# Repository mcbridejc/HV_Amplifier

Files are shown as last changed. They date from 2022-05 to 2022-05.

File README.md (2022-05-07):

High Voltage Amplifier
======================

A high-voltage amplifier takes a lower voltage input signal -- e.g. from a 
function generator of some sort -- and amplifies it to a high voltage. In this
case, the output range is -200V to +200V. High voltage amplifiers can be used
for a variety of applications, such as driving piezos, or digital microfluidics
electrodes. 

This board was created in KiCad 6.0.4. 

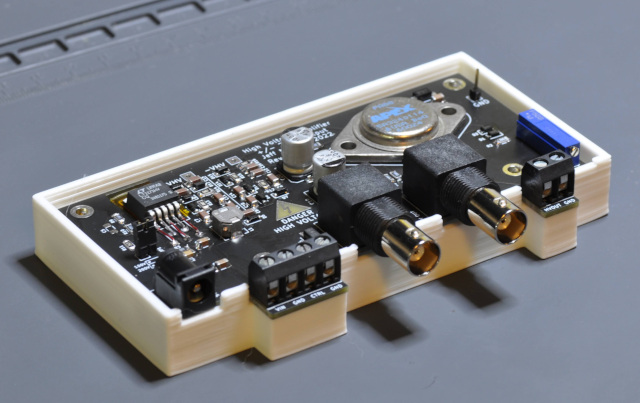
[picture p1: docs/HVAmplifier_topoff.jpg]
HV Amplifier


## A WARNING

This project can be dangerous. 200V is sufficient to kill you under
the right conditions. Even under the best conditions, it can give you a 
painful shock. You should not build this unless you know what you're doing.
If you do build this, you should handle it with caution. Be very careful about
what you touch when it is energized. Don't touch it with both hands
simultaneously. If you don't have to have it exposed, enclose it. Insulate
any wiring connected to the HV output.

## Description

This design uses the Apex PA88 high-voltage op-amp. These are fairly expensive
(~$250) at mouser, but I was able to find one for much cheaper on Ebay when I
built this. It also has a switching power supply which generates the positive
and negative high voltage rails from a 9V input. 

It can be operated at 100V, or 200V, based on whether the jumper JP1 is shorted.

The gain (Output voltage / control voltage) is adjustable from 15.9x to 60.2x,
using the potentiometer. At maximum gain, an input of 3.3V will provide an
output of 199V. 

When idle, it draws about 40mA when operating at 100V, and about 80mA at 200V. It
should be able to source about 4mA, although I have not tested under this kind
of load. For my application the current draw is much less. At some point I may
stress test it, but I am putting it off in case this test proves to be destructive!

## Enclosure 

I have provided some mesh files for a 3D printable enclosure. It requires some
M3 heat inserts (like [these](https://www.amazon.com/initeq-M3-0-5-Threaded-Inserts-Printing/dp/B073W2898C/))
and 18-23mm long M3 screws (like [these](https://www.amazon.com/M3-0-5-Stainless-Socket-Screws-Coverage/dp/B09B3992F4/)) 
to assemble. The STLs can be found in the [enclosure](enclosure/) directory.

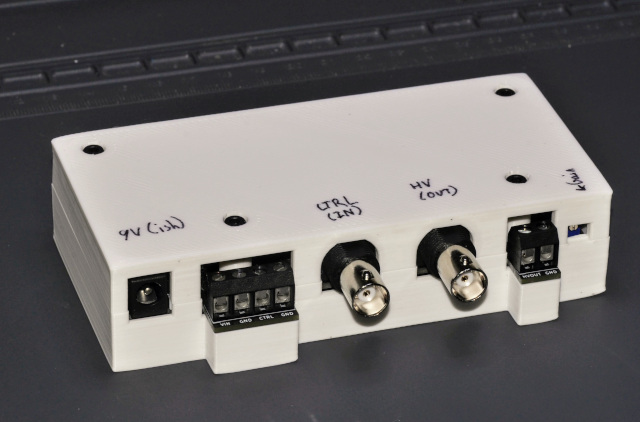
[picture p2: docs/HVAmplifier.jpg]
HV Amplifier


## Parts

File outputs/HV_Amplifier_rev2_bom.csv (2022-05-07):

Component | References | Value | Mfg Part Number | Package | Part Description | Voltage | Quantity Per PCB
1 | C3-C4 | 0.1u |  | 1206 | CAP CER 0.1UF 450V X7T 1206 | 450V | 2
2 | C6-C16 | 0.22u |  | 1206 | CAP CER 0.22UF 100V X7R 1206 | 100V | 11
3 | C19-C20 | 1.8u | UUB2G1R8MNL1GS |  |  | 400V | 2
4 | C17-C18 | 10u |  | 1206 | CAP CER 10UF 25V X5R 1206 | 25V | 2
5 | C1 | 15pF |  | 1206 | CAP CER 15PF 50V C0G/NP0 1206 | 50V | 1
6 | C2 | 1u |  | 1206 | CAP CER 1UF 16V X7R 1206 | 16V | 1
7 | D1-D2 D5-D15 | DSS120U | DSS120U | SOD-123F | SCHOTTKY 200V SOD-123FL |  | 13
8 | D16 | SMA6J5.0CA | SMA6J5.0CA | SMA | TVS DIODE 5VWM 9.2VC DO214AC TR |  | 1
9 | D3-D4 | SMAJ200A | SMAJ200A-TP | SMA | TVS DIODE 200V 324V DO214AC |  | 2
10 | J2 J4 | BNC | RF1-01K-D-00-50-BK-HDW |  | BNC RA PCB 50 4GHZ ZINC BODY NI |  | 2
11 | J3 | Barrel_Jack_Switch | PJ-202AH |  | CONN PWR JACK 2X5.5MM KINKED PIN |  | 1
12 | J1 | CTRL_TERM | 31101104 |  | TERM BLK 4P SIDE ENT 5.08MM PCB |  | 1
13 | J5 | Screw_Terminal_01x02 | 31101102 |  | TERM BLK 2P SIDE ENT 5.08MM PCB |  | 1
14 | JP1 | 100/200V SEL |  |  |  |  | 1
15 | L1 | 68uH | SPM6545VT-680M-D |  | FIXED IND 68UH 1.7A 340 MOHM SMD |  | 1
16 | R12-R16 | 10 |  | 1206 | RES 10 OHM 1% 1/4W 1206 |  | 5
17 | R1 R7 | 100 |  | 1206 | RES SMD 100 OHM 1% 1/4W 1206 |  | 2
18 | R8 R11 | 12.4k |  | 1206 | RES 12.4K OHM 1% 1/4W 1206 |  | 2
19 | R6 | 150 |  | 1206 | RES 150 OHM 1% 1/2W 1206 |  | 1
20 | R2 | 16.9k |  | 1206 | RES SMD 16.9K OHM 1% 1/4W 1206 |  | 1
21 | R3 | 1k |  | 1206 | RES 1K OHM 1% 1/2W 1206 |  | 1
22 | R4-R5 R9-R10 | 499k |  | 1206 | RES 499K OHM 1% 1/4W 1206 |  | 4
23 | RV1 | 50k | CT20EP503 |  | TRIMMER 50K OHM 0.5W PC PIN SIDE |  | 1
24 | U2 | LT117xHV | LT1171HVCQ |  | IC REG MULTI CONFG ADJ 5DDPAK |  | 1
25 | U1 | PA88 |  | TO-3-8 |  |  | 1
Component Groups: | 26
Component Count: | 62
Fitted Components: | 61
Number of PCBs: | 1
Total components: | 61
Schematic Version: | 2
Schematic Date: | 2022-05-06
PCB Variant: | [u'default']
BoM Date: | Fri 06 May 2022 05:38:52 PM PDT
Schematic Source: | HV_Amplifier.kicad_sch
KiCad Version: | Eeschema 6.0.4-6f826c9f35~116~ubuntu21.10.1

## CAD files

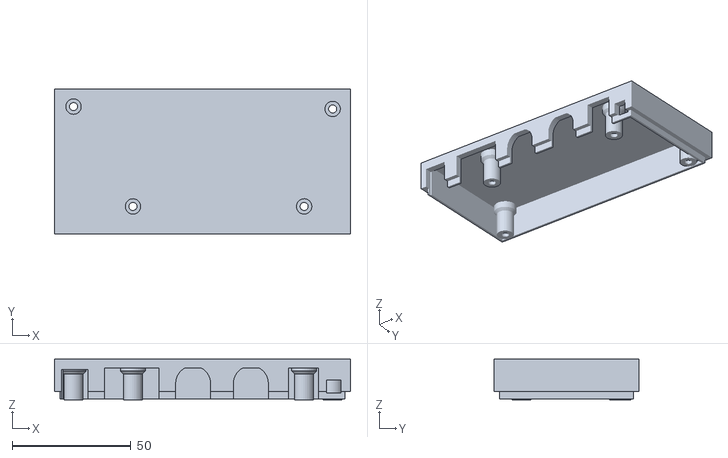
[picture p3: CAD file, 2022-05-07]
enclosure/HV_Amplifier_Enclosure_Top.stl
124.5 x 60.8 x 17.1

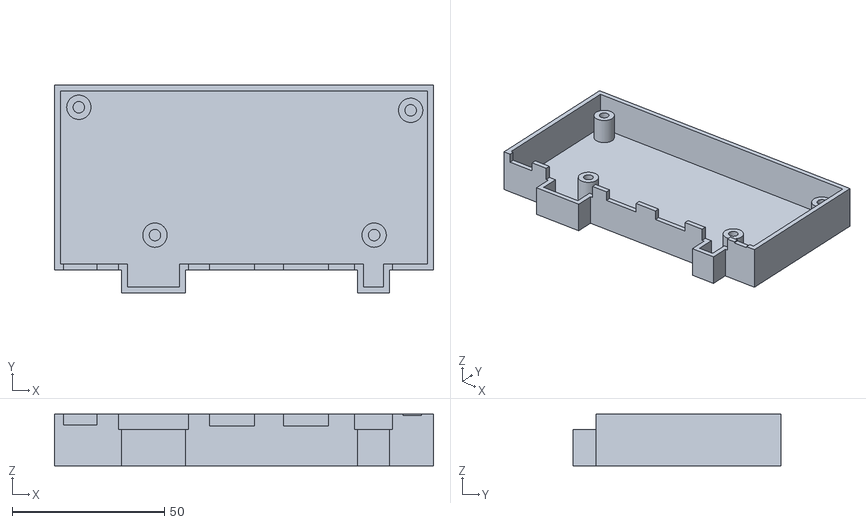
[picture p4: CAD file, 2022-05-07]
enclosure/HV_Amplifier_Enclosure_Bottom.stl
124.5 x 68.3 x 17.0

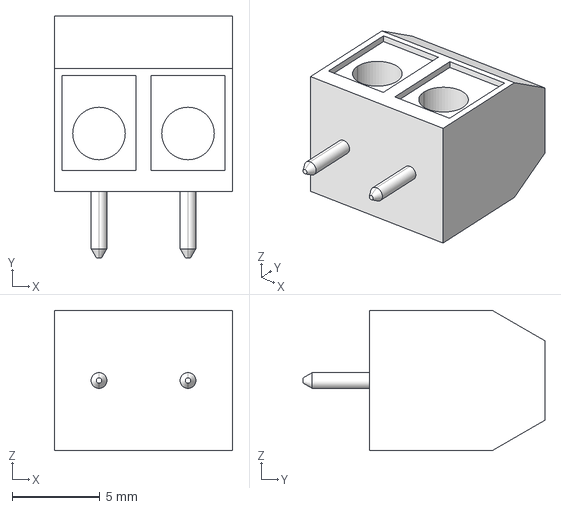
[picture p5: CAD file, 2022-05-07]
3dmodels/31101102.stp
10.2 x 13.8 x 8.00 mm

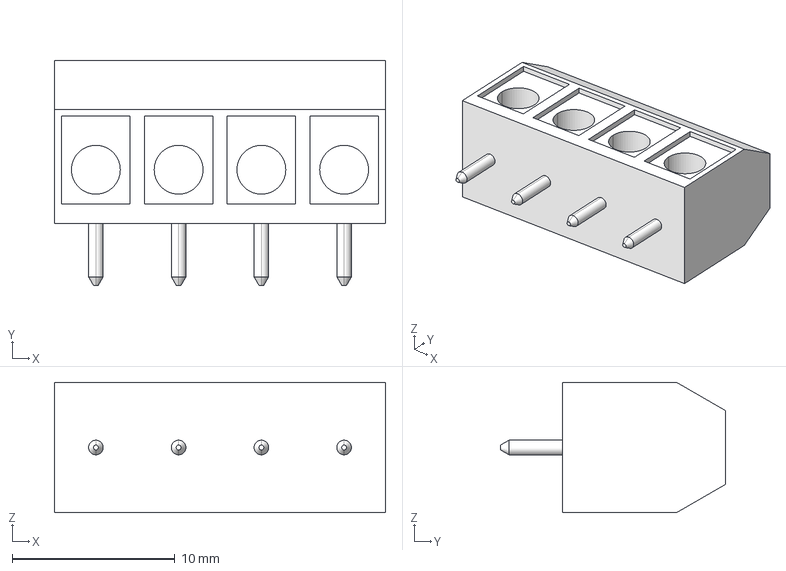
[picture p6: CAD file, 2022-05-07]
3dmodels/31101104.stp
20.3 x 13.8 x 8.00 mm

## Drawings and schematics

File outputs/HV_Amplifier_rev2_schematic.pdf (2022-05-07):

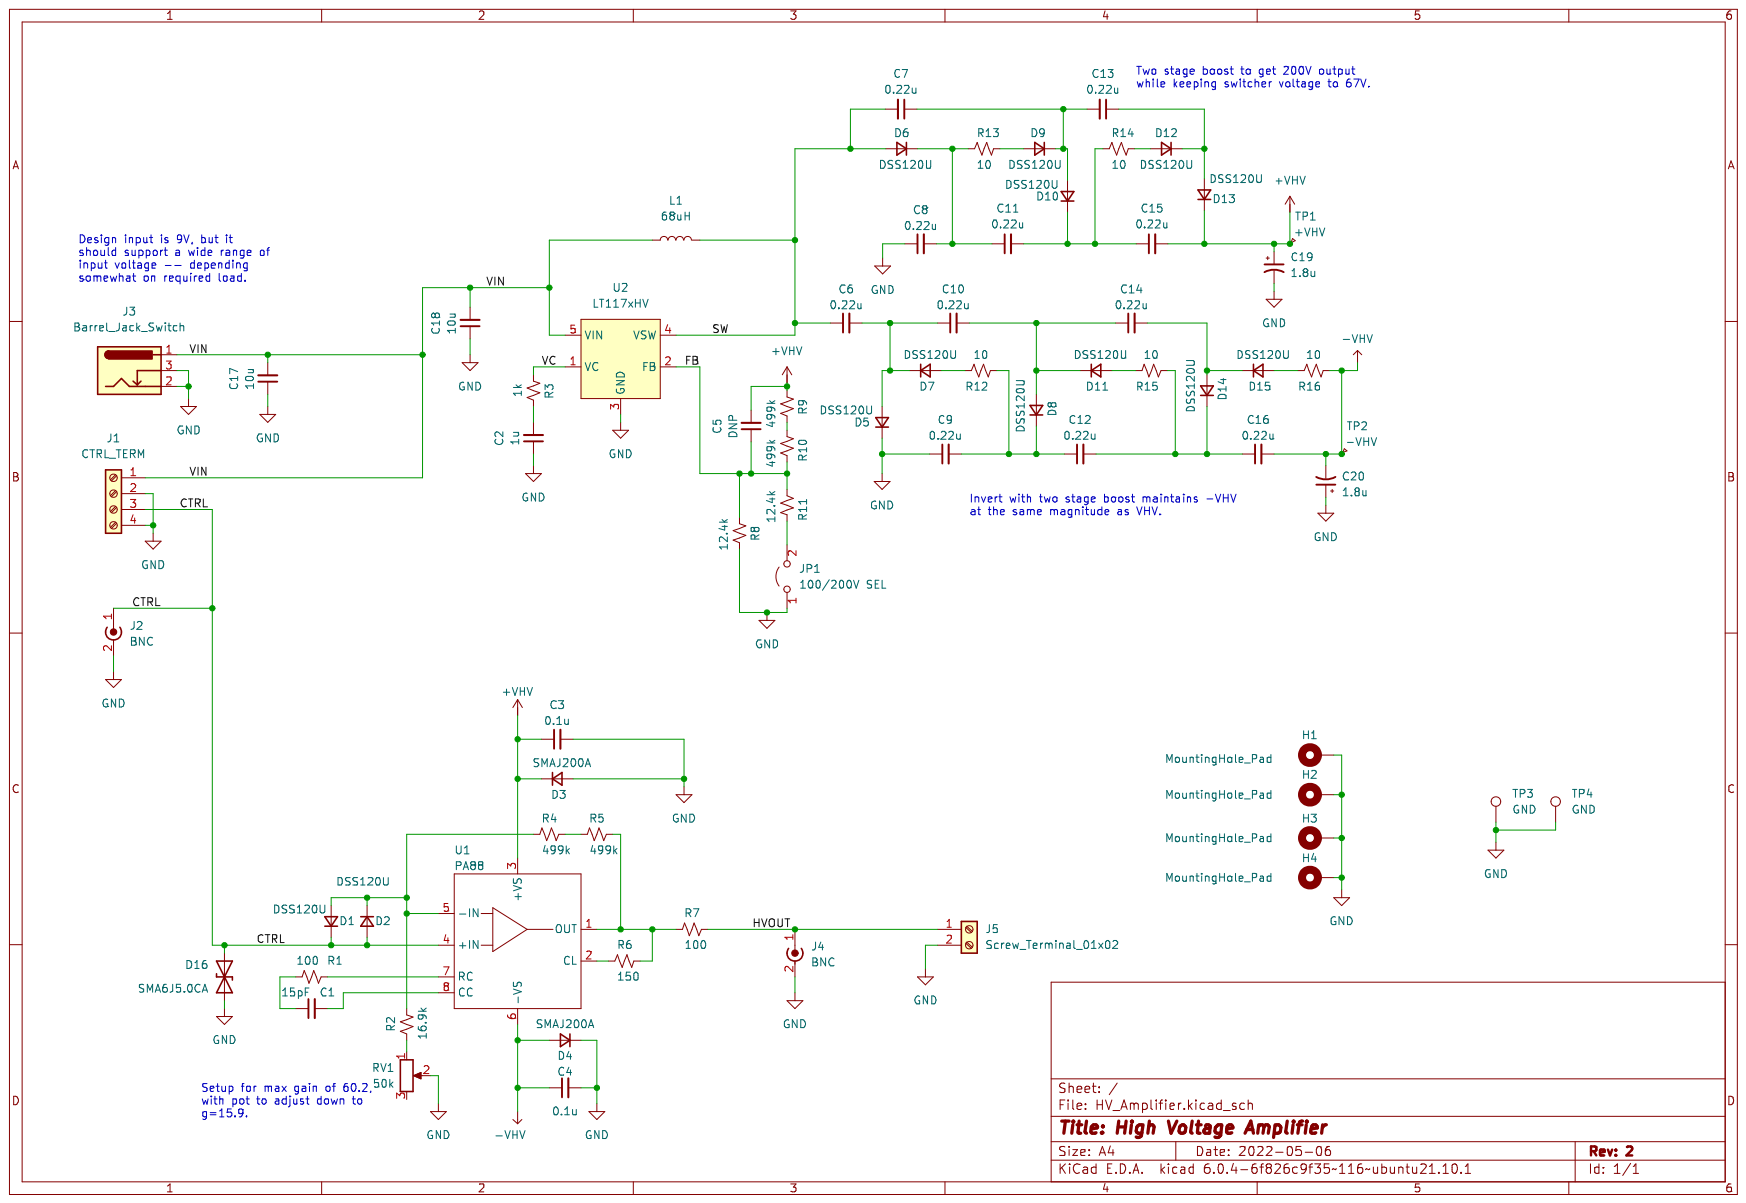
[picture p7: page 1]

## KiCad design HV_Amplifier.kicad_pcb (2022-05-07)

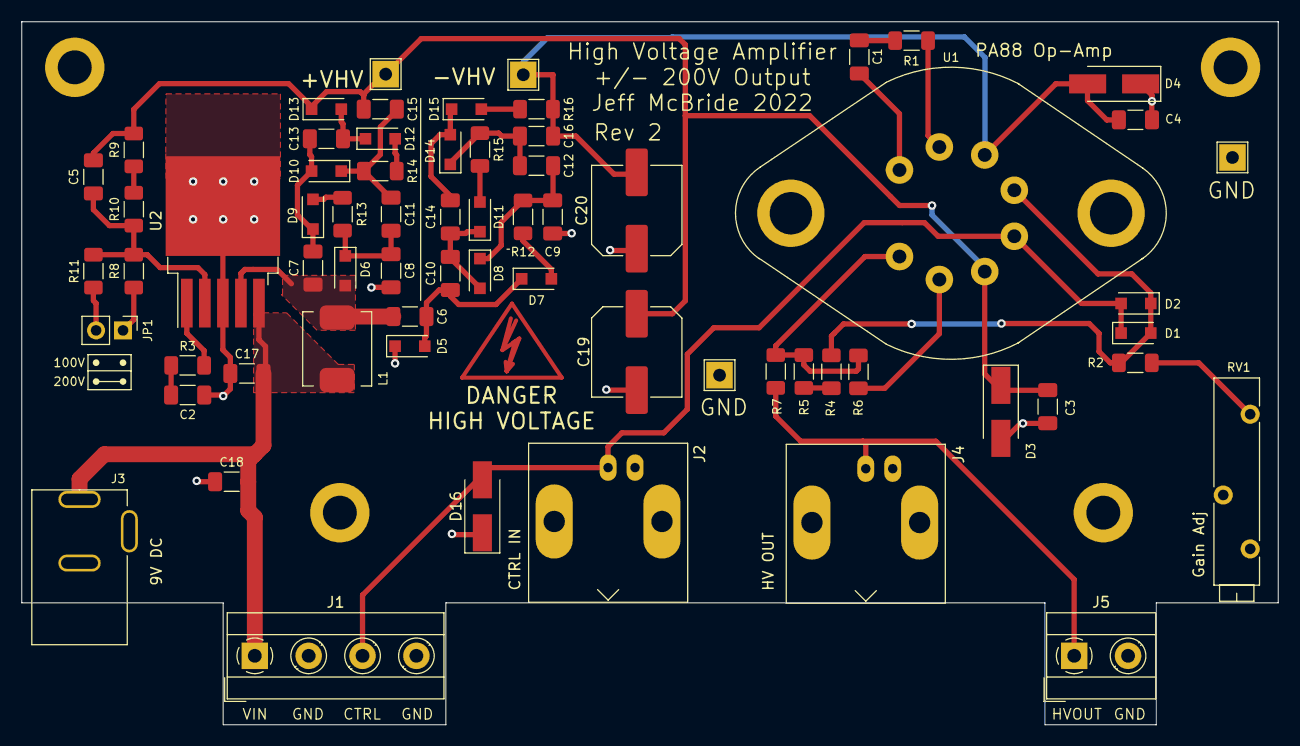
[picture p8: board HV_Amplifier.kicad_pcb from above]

Board: 2 copper layers, 118.5 x 66.3 mm, 70 parts (0 on the bottom side), 34 nets.

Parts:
C1: 15pF; C_1206_3216Metric_Pad1.33x1.80mm_HandSolder
C2: 1u; C_1206_3216Metric_Pad1.33x1.80mm_HandSolder
C3, C4: 0.1u; C_1206_3216Metric_Pad1.33x1.80mm_HandSolder
C5: DNP; C_1206_3216Metric_Pad1.33x1.80mm_HandSolder
C6, C7, C8, C9, C10, C11, C12, C13, C14, C15, C16: 0.22u; C_1206_3216Metric_Pad1.33x1.80mm_HandSolder
C17, C18: 10u; C_1206_3216Metric_Pad1.33x1.80mm_HandSolder
C19, C20: 1.8u; C_Elec_8x10.2
D1, D2, D5, D6, D7, D8, D9, D10, D11, D12, D13, D14, D15: DSS120U; D_SOD-123F
D3, D4: SMAJ200A; D_SMA_Handsoldering
D16: SMA6J5.0CA; D_SMA_Handsoldering
H1, H2, H3, H4: MountingHole_Pad; MountingHole_3.2mm_M3_DIN965_Pad
J1: CTRL_TERM; TerminalBlock_MetzConnect_Type101_RT01604HBWC_1x04_P5.08mm_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
J2, J4: BNC; BNC_Amphenol_B6252HB-NPP3G-50_Horizontal
J3: Barrel_Jack_Switch; PJ-202AH
J5: Screw_Terminal_01x02; TerminalBlock_MetzConnect_Type101_RT01602HBWC_1x02_P5.08mm_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
JP1: 100/200V SEL; PinHeader_1x02_P2.54mm_Vertical
L1: 68uH; Inductor_SPM6545_7x6.5
R1, R7: 100; R_1206_3216Metric_Pad1.30x1.75mm_HandSolder
R2: 16.9k; R_1206_3216Metric_Pad1.30x1.75mm_HandSolder
R3: 1k; R_1206_3216Metric_Pad1.30x1.75mm_HandSolder
R4, R5, R9, R10: 499k; R_1206_3216Metric_Pad1.30x1.75mm_HandSolder
R6: 150; R_1206_3216Metric_Pad1.30x1.75mm_HandSolder
R8, R11: 12.4k; R_1206_3216Metric_Pad1.30x1.75mm_HandSolder
R12, R13, R14, R15, R16: 10; R_1206_3216Metric_Pad1.30x1.75mm_HandSolder
RV1: 50k; Potentiometer_Bourns_3005_Horizontal
TP1: +VHV; TestPoint_THTPad_2.5x2.5mm_Drill1.2mm
TP2: -VHV; TestPoint_THTPad_2.5x2.5mm_Drill1.2mm
TP3, TP4: GND; TestPoint_THTPad_2.5x2.5mm_Drill1.2mm
U1: PA88; TO-3-8
U2: LT117xHV; TO-263-5_TabPin3

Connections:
+VHV: C3.1, C5.2, C15.2, C19.1, D3.1 (K), D13.1 (K), R9.2, TP1.1, U1.3 (+VS)
-VHV: C4.1, C16.2, C20.2, D4.2 (A), R16.2, TP2.1, U1.6 (-VS)
/CTRL: D1.1 (K), D2.2 (A), D16.2 (A2), J1.3, J2.1 (In), U1.4 (+IN)
/FB: C5.1, R8.2, R10.1, R11.2, U2.2 (FB)
/HVOUT: J4.1 (In), J5.1, R7.1
/SW: C6.1, C7.2, D6.2 (A), L1.2, U2.4 (VSW)
/VC: R3.2, U2.1 (VC)
/VIN: C17.2, C18.2, J1.1, J3.1, L1.1, U2.5 (VIN)
GND: C2.1, C3.2, C4.2, C8.1, C9.1, C17.1, C18.1, C19.2, C20.1, D3.2 (A), D4.1 (K), D5.1 (K), D16.1 (A1), H1.1, H2.1, H3.1, H4.1, J1.2, J1.4, J2.2 (Ext), J3.2, J3.3, J4.2 (Ext), J5.2, JP1.1 (A), R8.1, RV1.2, TP3.1, TP4.1, U2.3 (GND)
unnamed: C1.1, R1.1
unnamed: C1.2, U1.8 (CC)
unnamed: C2.2, R3.1
unnamed: C6.2, C10.1, D5.2 (A), D7.1 (K)
unnamed: C10.2, C14.1, D8.2 (A), D11.1 (K)
unnamed: C8.2, C11.1, D6.1 (K), R13.2
unnamed: C11.2, C15.1, D10.1 (K), R14.2
unnamed: C9.2, C12.1, D8.1 (K), R12.2
unnamed: C12.2, C16.1, D14.1 (K), R15.2
unnamed: C13.1, D12.1 (K), D13.2 (A)
unnamed: C7.1, C13.2, D9.1 (K), D10.2 (A)
unnamed: C14.2, D14.2 (A), D15.1 (K)
unnamed: D1.2 (A), D2.1 (K), R2.1, R4.2, U1.5 (-IN)
unnamed: D7.2 (A), R12.1
unnamed: D9.2 (A), R13.1
unnamed: D11.2 (A), R15.1
unnamed: D12.2 (A), R14.1
unnamed: D15.2 (A), R16.1
unnamed: JP1.2 (B), R11.1
unnamed: R1.2, U1.7 (RC)
unnamed: R2.2, RV1.1
unnamed: R4.1, R5.2
unnamed: R5.1, R6.1, R7.2, U1.1 (OUT)
unnamed: R6.2, U1.2 (CL)
unnamed: R9.1, R10.2

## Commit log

2022-05-07 Commit rev 2 of the board, which fixes a few issues from rev 1:
    - Change to SMD regulator footprint
    - Correct capacitor polarity on C19/C20
    - Flip pins on PA88 (so you can mount it on the top, as intended)
    [31101102.stp, 31101104.stp, HV_Amplifier-B_Cu.gbr, HV_Amplifier-B_Mask.gbr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]
2022-05-07 Add README and enclosure models
    [HV_Amplifier_Enclosure_Bottom.stl, HV_Amplifier_Enclosure_Top.stl]
2022-05-08 Add LTSpice circuit
